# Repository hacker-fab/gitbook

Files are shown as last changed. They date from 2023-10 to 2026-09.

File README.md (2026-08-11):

---
description: the first open-source semiconductor fab.
layout:
  width: default
  title:
    visible: false
  description:
    visible: false
  tableOfContents:
    visible: true
  outline:
    visible: true
  pagination:
    visible: false
  metadata:
    visible: true
  tags:
    visible: true
  actions:
    visible: true
---

# Hacker Fab Documentation

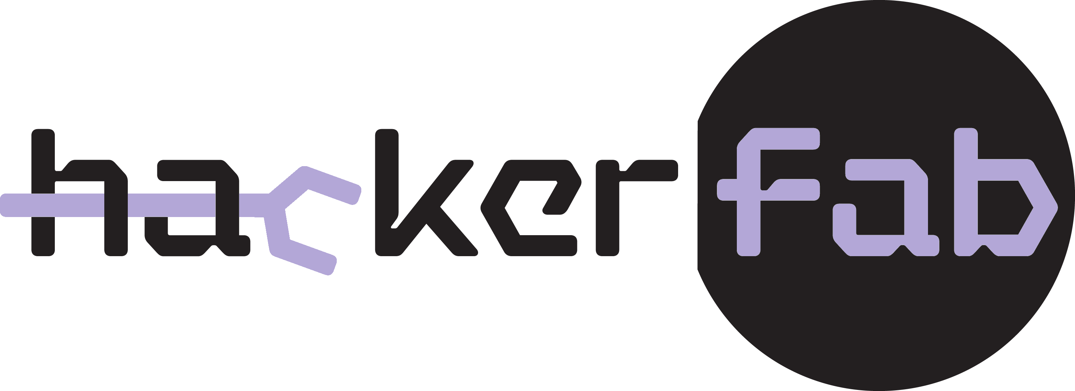
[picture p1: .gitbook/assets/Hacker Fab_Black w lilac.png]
<figure><figcaption></figcaption></figure>

<table data-view="cards"><thead><tr><th align="center"></th><th data-hidden data-card-target data-type="content-ref"></th><th data-hidden data-card-cover data-type="files"></th></tr></thead><tbody><tr><td align="center">discord.</td><td><a href="https://discord.gg/HFb3FKAxuX">https://discord.gg/HFb3FKAxuX</a></td><td></td></tr><tr><td align="center">github.</td><td><a href="https://github.com/hacker-fab">https://github.com/hacker-fab</a></td><td></td></tr><tr><td align="center">x.</td><td><a href="https://x.com/TheHackerFab">https://x.com/TheHackerFab</a></td><td></td></tr></tbody></table>

## <mark style="color:purple;">intro.</mark>

Our Goals:

1. Make a DIY version of every nanofabrication tool
2. Get there with collaborative open source hardware

Nanofabrication labs are expensive and inaccessible. Even STEM students at "prestigious institutions" have limited - if any - access to nanofabrication tools. Chips run our world. Everyone deserves access to the tools that make them. To ensure this level of access; cheap, open source, and easily replicable nanofabrication tools are needed. Labs that make and utilize these open source tools need to appear world wide. Hacker Fab is the open source fab project making this happen. As of August 2026, [**ten** Hacker Fabs have been established](https://app.gitbook.com/s/XgXjz6D0Vz2o0EOp8JO5/individual-fab-information), while others are underway. Multiple critical open source fab tools have been built, documented, and duplicated. Countless devices have been demonstrated with these tools, with documented process development.

Hacker Fab is made possible by a delocalized community of contributors. Hacker Fab can only grow to its full potential by gaining more contributors. Anyone can contribute, see the next section to learn how.

***

## <mark style="color:purple;">contributing to the hacker fab.</mark>

We communicate over [**Discord**](https://discord.gg/HFb3FKAxuX).

You don't need to build an entire fab to contribute, [**although you can**](guides/build-a-fab-to-do.md).

Read the [contribution guidelines](guides/required-reading-todo.md).

You don't need prior nanofabrication experience to create meaningful contributions.

#### How to add your work to the gitbook:

1. Hit the button that says "contribute"
2. Find the appropriate spot in the gitbook to add your work. For new projects this may be a new page, for modifications to existing work this could be an edit or amendment to existing pages. Fill in your contributed content.
   1. Note, if you download your working document(s) (google docs for example) as zipped .html files, you can them import them directly to a new gitbook page. This will maintain most of the content and formatting from your working document(s).
3. Submit a merge request; select Jay Kunselman and Alexander Hakim as reviewers.
4. Expect a message approving your merge request, or asking for revisions to your merge request.

***

## this website.

This page is a home for all shared documentation. There are enough resources here to turn an empty room into one that fabricates simple IC's in a matter of months.&#x20;

Many pages are works-in-progress. It is natural for individual contributors' work-in-progress notes to exist on google drive, notion, etc. Links to these exist at the top of each page, however these notes **move to Gitbook as soon as possible**.

Any contributor can submit change requests with a free Gitbook account. All of this is on Github, but formatted nicely here on Gitbook. You can contribute directly through Github as well.

For the most up-to-date status on everything, join the [**Discord**](https://discord.gg/HFb3FKAxuX).

***

## fab toolkit.

<table data-view="cards"><thead><tr><th></th><th></th><th></th><th></th><th></th><th></th><th data-hidden data-card-cover data-type="files"></th><th data-hidden data-card-target data-type="content-ref"></th></tr></thead><tbody><tr><td>Lithography Stepper V2</td><td><a href="fab-toolkit/patterning/lithography-stepper-v2-build-work-in-progress.md">Build </a>for $3,015</td><td><a href="standard-operating-procedures/patterning-sop-stepper-v2/">SOP</a></td><td>Carnegie Mellon</td><td></td><td></td><td><a href=".gitbook/assets/IMG_6328 (1).jpg">IMG_6328 (1).jpg</a></td><td><a href="fab-toolkit/patterning/lithography-stepper-v2-build-work-in-progress.md">lithography-stepper-v2-build-work-in-progress.md</a></td></tr><tr><td>Vacuum Spin Coater V1</td><td><a href="fab-toolkit/deposition/spin-coater-v1-build-to-do.md">Build</a> for $200</td><td><a href="standard-operating-procedures/patterning-sop-stepper-v2/vacuum-spin-coater-sop.md">SOP</a></td><td>Carnegie Mellon</td><td></td><td></td><td><a href=".gitbook/assets/spinner.jpg">spinner.jpg</a></td><td><a href="fab-toolkit/deposition/spin-coater-v1-build-to-do.md">spin-coater-v1-build-to-do.md</a></td></tr><tr><td>RF Sputtering Chamber</td><td>Build Chamber + Magnetron for $1,000</td><td>Build Power supply for $1,000 </td><td>Buy dual gas supply components for $5,000</td><td>Buy pumping system + gauge for $11,400</td><td>Carnegie Mellon</td><td><a href=".gitbook/assets/IMG_7063.jpg">IMG_7063.jpg</a></td><td></td></tr><tr><td>Thermal Evaporator V1 (work in progress)</td><td><a href="fab-toolkit/deposition/thermal-evaporator-v1-build-to-do.md">Build</a> for $15,000</td><td><a href="standard-operating-procedures/evaporator-sop.md">SOP</a></td><td>Carnegie Mellon</td><td></td><td></td><td><a href=".gitbook/assets/assembled.PNG">assembled.PNG</a></td><td><a href="fab-toolkit/deposition/thermal-evaporator-v1-build-to-do.md">thermal-evaporator-v1-build-to-do.md</a></td></tr><tr><td>Tube Furnace V1 (work in progress)</td><td><a href="https://youtu.be/oqOlrGPgng8?si=W4bGpYOg1724bw0Y">Build</a> for $200</td><td><a href="standard-operating-procedures/tube-furnace-sop.md">SOP</a></td><td>Projects in Flight</td><td></td><td></td><td><a href=".gitbook/assets/furnace.jpg">furnace.jpg</a></td><td><a href="https://www.youtube.com/watch?v=oqOlrGPgng8">https://www.youtube.com/watch?v=oqOlrGPgng8</a></td></tr><tr><td>Plasma Etcher</td><td><a href="/broken/pages/yvoQ2rocFkLU37tvrgpo">Buy</a> for $17,400</td><td><a href="standard-operating-procedures/plasma-etcher-sop.md">SOP</a></td><td>Plasma Etch PE-25</td><td></td><td></td><td><a href=".gitbook/assets/pe25-large.png">pe25-large.png</a></td><td><a href="/broken/pages/yvoQ2rocFkLU37tvrgpo">Broken link</a></td></tr><tr><td>Hot Plate</td><td><a href="https://www.amazon.com/SainSmart-Soldering-Preheating-Preheater-Intelligent/dp/B08R6XFPKR/ref=sr_1_5?crid=GQGSA76ZKKCZ&#x26;keywords=mini%2Bhot%2Bplate%2Bsoldering&#x26;qid=1701728962&#x26;sprefix=mini%2Bhot%2Bplate%2Bsoldeirn%2Caps%2C71&#x26;sr=8-5&#x26;th=1">Buy</a> for $125</td><td></td><td></td><td></td><td></td><td><a href=".gitbook/assets/2023-12-04 17_30_26-mini hot plate in hand.jpg ‎- Photos (1).png">2023-12-04 17_30_26-mini hot plate in hand.jpg ‎- Photos (1).png</a></td><td></td></tr><tr><td>3-Axis Piezo Nanopositioner</td><td><a href="/broken/pages/gS2GTDFXlq9ndyX3LUl5">Build </a>for $500</td><td></td><td></td><td></td><td></td><td></td><td></td></tr><tr><td>Electroless Plating</td><td><a href="fab-toolkit/deposition/electroless-nickel-plating.md">Build </a>for $500</td><td></td><td></td><td></td><td></td><td></td><td></td></tr></tbody></table>

<table data-view="cards"><thead><tr><th></th></tr></thead><tbody><tr><td></td></tr></tbody></table>

### verification / metrology tools.

<table data-view="cards"><thead><tr><th></th><th></th><th></th><th data-hidden data-card-cover data-type="files"></th><th data-hidden data-card-target data-type="content-ref"></th></tr></thead><tbody><tr><td>Probe Station V1</td><td><a href="/broken/pages/sr6DcGPRSb3k0lFNFZQW">Buy </a>for $15,800</td><td><a href="standard-operating-procedures/probe-station-sop.md">SOP</a></td><td><a href=".gitbook/assets/proberMPI-TS50.jpg">proberMPI-TS50.jpg</a></td><td><a href="/broken/pages/sr6DcGPRSb3k0lFNFZQW">Broken link</a></td></tr><tr><td>DIY SMU</td><td>Buy for $800</td><td><a href="fab-toolkit/metrology-characterization/semiconductor-parameter-analyzer/smu-analog-discoveries.md">SOP</a></td><td><a href=".gitbook/assets/AD3.png">AD3.png</a></td><td></td></tr><tr><td>Optical Spectrometer</td><td></td><td></td><td></td><td></td></tr></tbody></table>

### chemicals.

<table data-view="cards"><thead><tr><th></th><th></th><th></th></tr></thead><tbody><tr><td>Photoresists + Developers</td><td></td><td></td></tr><tr><td>Dielectrics</td><td></td><td></td></tr><tr><td>Conductors</td><td></td><td></td></tr><tr><td>Etchants</td><td></td><td></td></tr><tr><td>Dopant Sources</td><td></td><td></td></tr></tbody></table>

***

## background and licensing.

The Hacker Fab was inspired by [Sam Zeloof](https://www.youtube.com/@SamZeloof).

The Hacker Fab was started by Elio Bourcart, Alexander Hakim, and Sam Zeloof at Carnegie Mellon University (Thank you to CMU ECE dept, who's support catalyzed the project).

The first [Hacker Fab @ CMU](https://hackerfab.ece.cmu.edu/) is and currently managed by Matthew Moneck, Tathagata Srimani, and Jay Kunselman.

By default, all contributions use the following license stack, but may carry an additional NOTICE file depending on the origin of the contribution.

<details>

<summary>Hardware: CERN-OHL-W</summary>

For example, if you release HDL files under CERN-OHL-W and then somebody uses those files in their FPGA, when they distribute the bitstream (either putting it online or shipping a product with it) they do not to make the rest of the HDL design available under CERN-OHL-W as well.&#x20;

[https://ohwr.org/project/cernohl/wikis/faq#q-what-are-all-these-suffixes  ](https://ohwr.org/project/cernohl/wikis/faq#q-what-are-all-these-suffixes)

[https://ohwr.org/cern\_ohl\_w\_v2.pdf](https://ohwr.org/cern_ohl_w_v2.pdf)

</details>

<details>

<summary>Software: MPL v2.0</summary>

The MPL’s “file-level” copyleft is designed to encourage contributors to share modifications they make to your code, while still allowing them to combine your code with code under other licenses (open or proprietary) with minimal restrictions.&#x20;

[https://www.mozilla.org/en-US/MPL/2.0/ ](https://www.mozilla.org/en-US/MPL/2.0/)

[https://www.mozilla.org/en-US/MPL/2.0/FAQ/](https://www.mozilla.org/en-US/MPL/2.0/FAQ/)

</details>

<details>

<summary>Documentation: CC BY-SA 4.0</summary>

This license enables reusers to distribute, remix, adapt, and build upon the material in any medium or format, **so long as attribution is given to the creator**. The license allows for commercial use. If you remix, adapt, or build upon the material, you must license the modified material under identical terms. [https://creativecommons.org/licenses/by-sa/4.0/ ](https://creativecommons.org/licenses/by-sa/4.0/)[https://creativecommons.org/share-your-work/cclicenses/](https://creativecommons.org/share-your-work/cclicenses/)

</details>

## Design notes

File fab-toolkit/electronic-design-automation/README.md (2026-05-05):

---
icon: layer-group
---

# Electronic Design Automation

<table data-view="cards"><thead><tr><th></th><th data-type="content-ref"></th></tr></thead><tbody><tr><td>Mask Generation and DRC</td><td><a href="mask-generation-and-drc.md">mask-generation-and-drc.md</a></td></tr><tr><td>Device Modeling</td><td><a href="device-modeling.md">device-modeling.md</a></td></tr><tr><td>MagicVLSI</td><td><a href="magicvlsi-drc-and-lvs-wip.md">magicvlsi-drc-and-lvs-wip.md</a></td></tr></tbody></table>

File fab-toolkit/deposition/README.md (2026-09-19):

# 🧱 Deposition

<table data-view="cards"><thead><tr><th></th><th data-type="content-ref"></th></tr></thead><tbody><tr><td>Sputtering</td><td><a href="diy-rf-sputtering-chamber-cmu/">diy-rf-sputtering-chamber-cmu</a></td></tr><tr><td>ALD</td><td><a href="diy-ald/">diy-ald</a></td></tr></tbody></table>

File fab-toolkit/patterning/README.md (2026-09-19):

---
layout:
  width: default
  title:
    visible: true
  description:
    visible: true
  tableOfContents:
    visible: true
  outline:
    visible: true
  pagination:
    visible: false
  metadata:
    visible: true
  tags:
    visible: true
  actions:
    visible: true
  anchors:
    visible: true
---

# 🎥 Patterning

**For a description of what the team at CMU is working on in Spring 2025, check out** [**this document**](https://docs.google.com/document/d/1cksUbf5onK4FIIpE_ZZxUgtdfJ7OKFyU2kt76BniGkw/edit?usp=sharing)**!**

Goals of this page:

* Not to try and cover theory or industry standard, but to break the problem into first principles just enough to give context to the quantifiable parameters
* Also an opportunity to frame the problem wide enough to set the tone of thinking of these machines from the ground up (aligned with goal, don't think of industry as immutable)
* Exhaustive list of industry methods and examples
* Quantifiable end user parameters with descriptions + standardized tests

***

## Background

#### Overview

A photolithography stepper is a machine that exposes a pattern of light onto a layer of photoresist chemical on the wafer, then ‘steps’ over to the next pattern. Before each exposure, it must align with previous patterns on the wafer so that each layer of the device is in the correct position relative to the previous. The accuracy with which it can do this is called “alignment accuracy”. Alignment accuracy and optical resolution are the two most important metrics of a stepper’s performance.

There are 2 main components of our stepper: the light source and optics, and then the mechanical micropositioning stage that moves the chip itself. Alignment accuracy is a function of both the mechanical micropositioning stage and the reliability of the projector’s optomechanical components.

#### Masked vs. Maskless Lithography Systems

Commercial lithography machines use photomasks to create the image, typically made of chrome on glass. Instead, our Maskless Photolithography Stepper uses a DLP projector to create a pattern. This allows us to change patterns instantly, opening the option up for advanced techniques like tiling (making a circuit larger than one exposure field).

## Quantifiable Parameters

#### Functional Specifications: The End Product&#x20;

<details>

<summary>Developed Resolution</summary>

describe out standardized test: darkfield/brightfield, developed with AZ400K for 80s, measured pitch distance, used airforce test pattern

**Value**:&#x20;

**Tools Required for Verification**:&#x20;

**Method of Verification**:&#x20;

**Possible Variation**: Error during development (see [Patterning SOP](../../standard-operating-procedures/patterning-sop-stepper-v2/patterning-sop-stepper-v1.md))

**References**: _pics/videos_

</details>

<details>

<summary>Automation Capabilities / Throughput</summary>

what human actions are required: manual loading/unloading, choose the pattern, align manually or automatically with software

approximate area exposed per second

how much time to do one exposure, how much of that is active work vs. waiting around

</details>

&#x20;**Patterning Machine Specifications:**&#x20;

<details>

<summary>Optical Resolution</summary>

**Tools Required for Verification**: Microscope + Calibrated Camera to convert pixels to μm

**Method of Verification**: _make another page for optical resolution test?_

**Possible Variation**: misalignment of optics during assembly

**References**: _pics/_[_videos_](#user-content-fn-1)[^1]

</details>

<details>

<summary>Developed Resolution</summary>

**Tools Required for Verification**:&#x20;

**Method of Verification**:&#x20;

**Possible Variation**: Error during development (see [Patterning SOP](../../standard-operating-procedures/patterning-sop-stepper-v2/patterning-sop-stepper-v1.md))

**References**: _pics/videos_

</details>

<details>

<summary>Single Exposure Area</summary>

</details>

<details>

<summary>Approximate Exposure Time (for AZ P4210 photoresist)</summary>

**Tools Required for Verification**: AZ400K Developer Solution + Microscope

**Method of Verification**:&#x20;

**Possible Variation**: Can vary UV LED power and beam splitter ratio to decrease/increase exposure time

**References**: _pics/videos_

</details>

<details>

<summary>Mechanical Resolution - Step Size</summary>

</details>

<details>

<summary>Mechanical Resolution - Repeatability</summary>

</details>

<details>

<summary>Maximum Wafer Size</summary>

</details>

[^1]:

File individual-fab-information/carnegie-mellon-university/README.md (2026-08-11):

# Carnegie Mellon University

The [Hacker Fab @ CMU](https://hackerfab.ece.cmu.edu/) is the birthplace of the Hacker Fab initiative, and operates as an integrated course + lab. The course covers nanofabrication and device fundamentals. Students spend the majority of their time working on a project that adds a new tool/process to the fab or improves an existing one. Additionally, students participate in labs where they use the DIY tools to fab and characterize devices.

Contact(s):

* Joel Gonzalez (bgonzale@andrew.cmu.edu)
* Icey Chen (yanbing@andrew.cmu.edu)
* Rahim Malik (rahimm@andrew.cmu.edu)
* Jay Kunselman (jskunsel@andrew.cmu.edu)
* Kent Wirant (jwirant@andrew.cmu.edu)

Tooling in use:

* DIY Litho Stepper
* DIY RF Sputtering
* DIY Evaporator
* DIY Spin coater
* 2 fume hoods (lab infrastructure)
* Purchased Plasma Etcher
* Purchased Tube Furnace

Verified device capabilities:

* NMOS, 5um gate length (based on P type wafers with SiO2 and PolySi pre-fabbed by WaferPro)
* MOSCaps
* Resistors
* Diodes
* Inverters
* NAND gates

Tooling in progress:

* ALD
* 2D crystal stacking robot
* Automated Sputtering
* Automated Litho Stepper
* EDA tools

Device capabilities in progress:

* PMOS, CMOS (with in-house sputtered gate stack)

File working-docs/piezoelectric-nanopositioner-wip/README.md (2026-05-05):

# Nanopositioner - WIP

This project builds on previous work done at HackerFab, as well as concepts described in the [following paper](https://www.sciencedirect.com/science/article/pii/S2468067222000621).

Based on those designs, we decided to go with a similar mechanical approach, focusing on simplicity, compactness, and the ability to iterate quickly.

### **What it is**

This is a compact nanopositioner designed for precise motion control using a piezo actuator. The system is intended for applications like STM, optics alignment, and general nanometer-scale positioning tasks.

The mechanical design is based on linear guides using ceramic ball bearings (G5 Si₃N₄), which provide smoother and more stable motion over time compared to stainless steel balls (which tend to wear and degrade motion quality).

The current design uses:

* 2.778 mm ceramic balls
* stainless steel shafts (preferably hardened), Ø1.5 mm, length 24 mm
* thin positioning plates (\~0.25 mm) to constrain ball movement

The sliding interface is based on AlN (amorphous substrate) bonded to magnets and magnetic stainless steel (grade 430). Initially, motion is not perfectly smooth, but after a short “run-in” period (self-polishing), the system becomes significantly more stable.

<figure><figcaption></figcaption></figure>

### **Vacuum-first design**

From the beginning, this project is designed with **vacuum compatibility in mind**. That directly influences material and component choices.

We intentionally select materials that are:

* low outgassing
* mechanically stable under vacuum
* compatible with UHV-like environments (or at least not terrible in rough vacuum)

This is why we use:

* ceramic balls instead of lubricated bearings
* metal structural components instead of polymers where possible
* minimal use of adhesives (and only vacuum-compatible ones like Torr Seal where needed)
* materials like AlN for sliding interfaces

This constraint makes the design harder, but avoids having to redesign everything later for vacuum operation.

### **Piezo & Mechanics**

The actuator used is a PK2FMP2 piezo, mounted using end hemispheres and end cups. This mounting approach helps maintain alignment and reduces unwanted mechanical stress.

One critical aspect of this design is **maintaining strict axial alignment**, especially along the Z-axis.

Any deviation from the Z-axis introduces lateral forces, which:

* mechanically expand the structure
* couple motion into unwanted directions
* generate significant vibrations

This is one of the main limiting factors for stability and precision, and we are actively working on improving this.

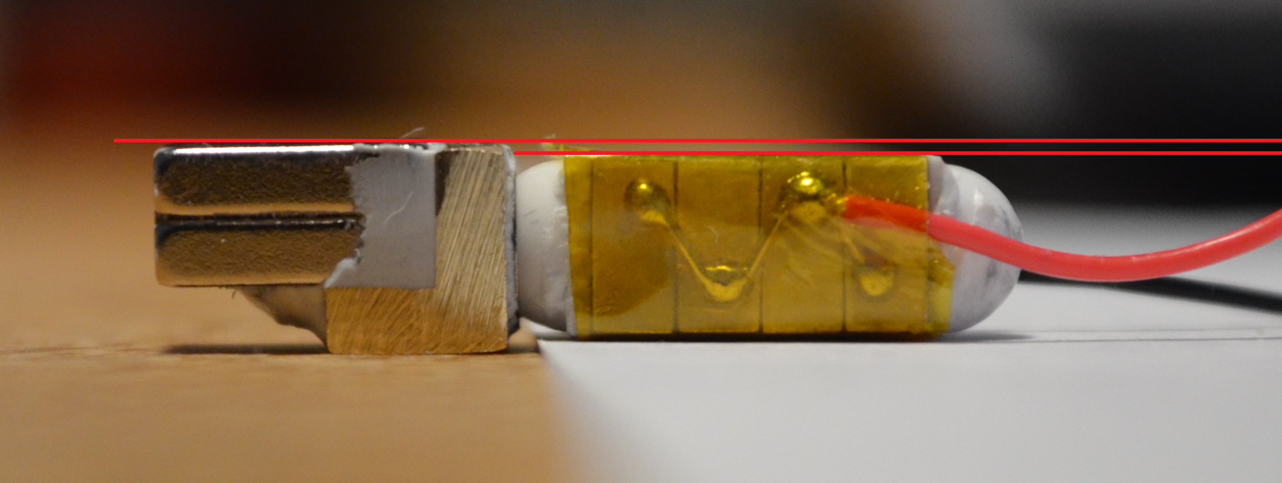
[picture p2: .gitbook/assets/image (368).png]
<figure><figcaption></figcaption></figure>

### **Electronics (WIP)**

We are currently redesigning the electronics with a focus on reducing cost and simplifying the system.

The first version of the board used **Apex PA441 amplifiers**, which cost around $25 per unit. This was originally chosen to support a wide voltage range (+100V / -50V).

However, after initial testing and switching to a different piezo, such a large range is no longer necessary. The current piezo operates up to **+60V**, which allows us to:

* simplify the driver design
* reduce cost significantly
* improve overall efficiency

We have already designed a new power supply providing **+60V / -30V**, which better matches the requirements of the current setup. At the moment, we are waiting for components to complete the new amplifier stage.

The system is designed with **opto-isolation (optocouplers)** to separate control electronics from the high-voltage section, improving robustness and reducing noise coupling.

<figure><figcaption></figcaption></figure>

### **Current Status**

This is an early prototype, but the mechanical concept is already working and gives promising results in terms of stability and resolution.

We are currently working on:

* improving electronics (cost + design)
* refining mechanical alignment (especially Z-axis stability)
* integrating an encoder (MT6835) for feedback and control

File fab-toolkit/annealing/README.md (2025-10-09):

# 🛠️ Annealing

<table data-view="cards"><thead><tr><th></th><th data-type="content-ref"></th></tr></thead><tbody><tr><td>Tube Furnace</td><td><a href="tube-furnace/">tube-furnace</a></td></tr></tbody></table>

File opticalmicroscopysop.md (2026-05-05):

# OpticalMicroscopySOP

**Document ID:** HF-QC-MIC-004\
**Prepared by:** Shreeja Gupta\
**Version:** 1.0\
**Date:** March 2, 2026

## 1. Purpose

To inspect patterned wafers using optical microscopy to verify feature quality, alignment, and dimensions after lithography and development.

Supports HackerFab fabrication workflows targeting <10 µm feature sizes using calibrated microscope measurements.

## 2. Scope

Applies to:

* Wafers after development (HF-PROC-DEV-003)
* Lithography calibration wafers
* Feature size verification and process troubleshooting

## 3. Responsibilities

* Operator: Inspect wafer and record measurements.
* Process Lead: Maintain calibration accuracy.
* Team Lead: Review results for process improvements.

## 4. Equipment & Materials

### Equipment

* Optical microscope (AmScope)
* Amscope measurement software
* Microscope stage
* Cleanroom wipes
* Computer for image capture

### Materials

* Patterned wafer
* Calibration slide (µm scale)

## 5. Safety Precautions

* Handle wafers with tweezers only.
* Avoid touching lens surfaces.
* Do not drop wafers on stage.
* Turn off illumination after use.

## 6. Calibration Requirements

Before measuring feature sizes:

1. Use a calibration slide with known µm markings.
2. Calibrate at each magnification level used.
3. Save calibration settings in software.

## 7. Procedure

{% stepper %}
{% step %}
#### 7.1 Setup

1. Turn on microscope illumination.
2. Select 5x magnification
3. Place wafer on stage.
{% endstep %}

{% step %}
#### 7.2 Focus and Locate Pattern

1. Focus using the coarse knob.
2. Adjust fine focus until the pattern is sharp.
{% endstep %}

{% step %}
#### 7.3 Inspect Pattern Quality

Check for:

* Clean edges
* No overdevelopment
* Uniform exposure
{% endstep %}

{% step %}
#### 7.4 Measure Feature Size

1. Use a calibrated measurement slide.
2. Measure multiple features.
3. Record average feature size.

Example:

* Measured smallest feature = 8.7 µm
{% endstep %}

{% step %}
#### 7.5 Capture Images

1. Save screenshots at100% zoom (important for accurate scaling).
2. Include a scale bar.
3. Name the file with the date.

Example:2026-03-02\_HFLogo\_8sExposure\_4000rpm.png
{% endstep %}
{% endstepper %}

## 8. Expected Results

* Sharp, well-defined patterns.
* Feature sizes within the expected range.
* Verification of lithography calibration.

## 9. Troubleshooting

| Problem               | Cause             | Fix                    |
| --------------------- | ----------------- | ---------------------- |
| Blurry image          | Out of focus      | Refocus stage          |
| Wrong feature size    | Calibration error | Recalibrate microscope |
| Uneven patterns       | Spin coat issue   | Check SC SOP           |
| Overdeveloped pattern | Too long dev time | Adjust DEV SOP         |

## 10. Notes

* Always recalibrate after changing magnification.
* Keep image records for process tracking.
* Use microscopy results to tune exposure dose and spin speed.

## 11. Revision History

| Version | Date          | Changes       |
| ------- | ------------- | ------------- |
| 1.0     | March 2, 2026 | Initial draft |

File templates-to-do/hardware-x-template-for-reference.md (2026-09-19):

---
hidden: true
---

# Hardware X Template (for reference)

<br>

1\.  Hardware in context

Write a short description of the hardware and provide context, i.e., describe similar open hardware and proprietary equipment in the field.

<br>

2\.  Hardware description

Describe your hardware, highlighting the customization rather than the steps involved in the procedure. Explain how  it  differs  from  other  hardware  and  the  advantages  it  offers  over  pre-existing  methods.  For  example,  how does this hardware compare to other hardware in terms of cost or ease of use, or how can it be used to develop further designs in a particular area?&#x20;

Add 3-5 bullet points which broadly explain to other researchers - inside or outside of the original user community - how the hardware could help them, with either standard or novel laboratory tasks.

<br>

Design files

Your design files should be editable - see OSHWA’s open source definition of ‘Documentation’ for further details. You must then either:

* Upload your design files to one of the three approved online repositories - Mendeley Data (instructions), the  Open  Science  Framework  (instructions)  or  Zenodo  (instructions).  We  recommend  this  option  as  the repositories support versioning of files.
* Upload your design files as supplementary materials (e.g., CAD files, videos. . . )  to Hardware X’s online editorial system when you submit your manuscript.
* Include your design files in the body of the manuscript (e.g., as figures).

<br>

CAD files:

You are encouraged to use free and open source software packages for creating the  files.  For  CAD files, OpenSCAD, FreeCAD, or Blender  are  encouraged, but, if these are  not  available, we accept source files from proprietary CAD packages, such as Autocad or Solidworks, and other drawing packages.

<br>

3D printing:

Supplementary files that facilitate digital replication of the devices are encouraged; for example, STL files for 3D printing components. We recommend uploading CAD files to the NIH 3D Print Exchange as Custom Labware and then entering the link here.

<br>

Electronics:

PCB layouts and other electronics design files can be uploaded to the Open Hardware  Repository or other repositories or as supplementary materials.

<br>

Software and firmware:

All software files used in the design and operation of the hardware should be included in the repository. Provide a description of the software and firmware and use extensive comments in the code.&#x20;

<br>

3\.  Design files summary

Complete a separate row for each design file associated with your hardware (including the primary design files). Any empty rows should be deleted.

<br>

<br>

| Design filename             | <p>File type</p><p><br></p>     | <p>Open source license</p><p><br><br></p>                                                                               | <p>Location of the file</p><p><br></p>                                                           |
| --------------------------- | ------------------------------- | ----------------------------------------------------------------------------------------------------------------------- | ------------------------------------------------------------------------------------------------ |
| For  example: Design file 1 | E.g. CAD  file, figures, videos | All designs must be submitted under an open hardware license.  Enter the corresponding open source license for the file | Either enter    the    URL for the  repository  or  the  sentence: ”Available with the article”. |

<br>

<br>

For each design file listed in the summary table above, include a short description of the file below (just one or two sentences per design file).

<br>

Bill of materials

If  your  bill  of  materials  is  long  or  complex,  you  can  upload  the  details  in  an  editable  spreadsheet, e.g., ODS file type, Excel spreadsheet or PDF file, to an open access online location, such as the Open Science Framework repository.  Include the link here.  Alternatively, the bill of materials can be submitted alongside your manuscript as supplementary material.

<br>

<br>

4\.  Bill of materials summary

Complete  a  separate  row  for  each  component  of  your  hardware  –  all  components  associated  with  a  cost  should be listed and any empty rows should be deleted.

<br>

<br>

| Designator                                                                                                                                                                                      | Component           | Number          | Cost per unit - currency            | <p>Total cost -currency</p><p><br></p> | Source of Materials                 | Material Type                                                                                                                                                                                                                             |
| ----------------------------------------------------------------------------------------------------------------------------------------------------------------------------------------------- | ------------------- | --------------- | ----------------------------------- | -------------------------------------- | ----------------------------------- | ----------------------------------------------------------------------------------------------------------------------------------------------------------------------------------------------------------------------------------------- |
| <p>If possible,</p><p>use the same designator  here as you use in the associated</p><p>design file.If that’s not possible, you will need to explain the  relationship</p><p>between the two</p> | Name of component 1 | Number of units | Cost per unit and the currency used | Total cost and the currency used       | If possible, direct purchasing link | <p>Select from:</p><p>-Metal</p><p>-Semi-</p><p>conductor</p><p>-Ceramic</p><p>-Polymer</p><p>-Biomaterial</p><p>-Organic</p><p>-Inorganic</p><p>-Composite</p><p>-Nanomaterial</p><p>-Semiconductor</p><p>-Non-specific</p><p>-Other</p> |

<br>

You can use this space for any additional descriptions of the materials used.

<br>

<br>

5\.  Build instructions

Provide detailed, step-by-step construction instructions for the submitted hardware:

* Include all necessary information for reproducing it.
* Explain and (when possible) characterize design decisions.  Include any design alternatives you created.
* Use visual instructions such as schematics, images and videos.
* Clearly reference design files and component parts described in the Design file summary and the Bill of materials summary
* Highlight any potential safety concerns.

<br>

6\.  Operation instructions

Provide detailed, step-by-step instructions for the safe and proper operation of the hardware.

* Use visual instructions, as necessary.
* Highlight any potential safety hazards.

<br>

7\.  Validation and characterization

Demonstrate the operation of the hardware and characterize its performance for a specific scientific application.

* Highlight a relevant use case.
* If possible, characterize performance of the hardware over operational parameters.
* Create a bulleted list describing the capabilities (and limitations) of the hardware.  For example, load and operation time, spin speed, coefficient of variation, accuracy, precision, etc

\
<br>

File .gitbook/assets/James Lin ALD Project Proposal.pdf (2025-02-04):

18-469D/18-669D - Hacker Fab | Spring 2025

# Proposal & Plan:

## ALD Precursor Delivery System

James Lin

## Background

The Precursor Delivery System is responsible for delivering the precursors of I2O3 and SnO2 (TMIn and TDMASn respectively), H2O, and the N2 carrier gas to the ALD chamber.

The delivery system is designed to pulse the precursor chemicals at specific pressures and time intervals to deliver the right chemical at each state of the deposition process. It is also designed to facilitate the flow of the carrier gas at a specific temperature and flow rate for both chemical delivery and purging on the wafer surface.

This is all done in order to facilitate the growth of high quality ITO thin films in the ALD chamber.

The delivery system must be rated and sealed for the overall vacuum requirement of the entire ALD system of 100 mTorr. In addition, due to the precursor chemicals being pyrophoric, materials that interact with the chemicals must also be considered in order to comply with lab safety requirements.

The overall ALD Delivery System will consist of two main parts:
- Delivery System
- Delivery Storage

1

## Delivery System

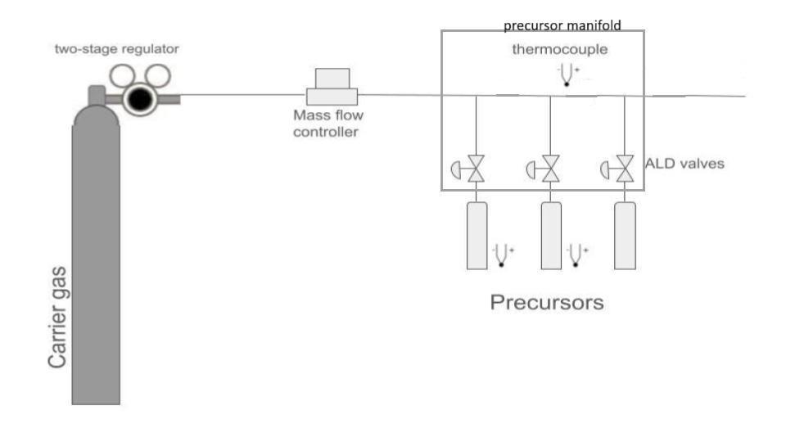
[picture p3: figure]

Technical requirements
- Material Selection:
- Compatible with pyrophoric chemicals and corrosion resistant
- Thermal:
- TMIn and TDMASn bubblers heated to 60C
- Needs possibility for 20C for TMIn and 45C for TDMASn
- Delivery line capable of maintaining fluid temperature of 60C up to ALD chamber
- Fluid Delivery and Vacuum:
- Delivery line rated for 100 mTorr vacuum
- Carrier gas delivered at 10 - 40 sccm
- Compatible with either N2 or Ar
- ALD valves able to pulse for 3-0.625 s
- Measurement:
- Thermocouple capable of accurate fluid temperature measurement
- Integration with DAQ and electronics
- Integration with the ALD chamber
- Minimize cost where possible

2

What has been completed/purchased
- Dual stage regulator (NOT ORDERED)
- Steps down from cylinder pressure (~2000 psi) to operating pressure for Mass Flow Controller (<70 psi)
- 100 SCCM flow controller
- Chemical ampules
- From CMU Nanofab
- Swagelok ALD3 valves and manifold
- From CMU Nanofab
- inlet = ¼” female VCR
- outlet = ¼” male VCR
- Stainless steel tubing
- Male and female VCR to male fittings
- VC face seal metal gaskets
- KF25 to ¼” tube fitting
- Interface with vacuum
- Heating tape (DOESN’T WORK)

Since most of the central components have already been procured and critical materials and fittings have been decided, further development would be focused on tube routing, possible thermal insulation, thermocouple integration, and construction.

3

Major deliverables
- Full CAD of delivery system
- Fittings locations and tubing geometry accurate to real life setup
- Communication with electronics for sensor placement and wiring plan
- Check for assembly operations and integration with Delivery Storage
- Assembly of delivery system
- Troubleshoot any potential problems with integrating electronics
- Testing for performance of assembly under vacuum
- Ensure that the system complies with safety and technical requirements during use
- Testing heating element and sensors
- Ensure temperature, flow rate, and pressure targets are met
- Ensure that controls are able to read accurate data
- Documentation
- Design process, analysis
- Manufacturing and assembly instructions
- BOM

Things to consider
- Overall dimensions of proposed locations of ALD station
- Heating should be maintained for all lines downstream of precursor
- Must avoid condensation and precursor build up so line doesn’t explode
- Thermocouple placement should be on tube surface as to not disrupt fluid

flow
- Research temperature values also measure at tube
- ¼” tube should not have steady state and conduction loss problems
- Operations of assembly
- We do not want to get tubings that don’t fit
- Integration with delivery storage and electronic components
- Heating block vs heating tape
- Heating block is made to fit manifold but very heavy
- Heating tape would need some thinking to figure out how to wrap manifold

4

## Delivery Storage

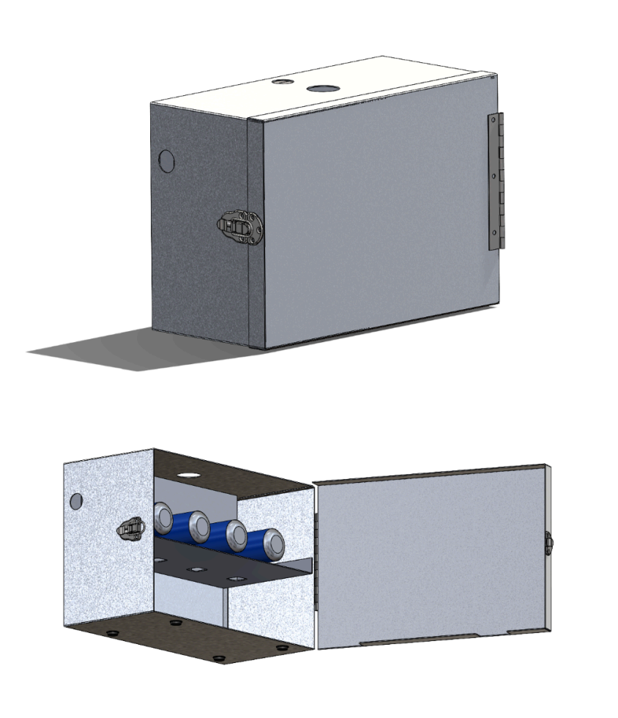
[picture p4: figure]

Technical Requirements
- Storage Capacity:
- Holds the precursor manifold with three ALD valves and three gas ampules
- Potentially has room for mass flow controller in the future
- Packaging:
- Contains holes to attach proper fittings for an exhaust connection, carrier gas inlet, and a gas outlet
- Potentially need pass throughs to account for wiring
- Leave room for either heating block or heating tape/alternative heating options
- Materials:
- Made out of aluminum for precursor compatibility
- Ergonomics:
- Ampoules should be easy to access in order for simpler replacement when necessary
- Manufacturing:
- Minimize time to manufacture and assemble
- Design needs to be easily replicable
- Allow design to be manufactured with precision
- Minimize cost

5

What has been completed/purchased
- Prototype enclosure partially made with bent sheet metal and riveted

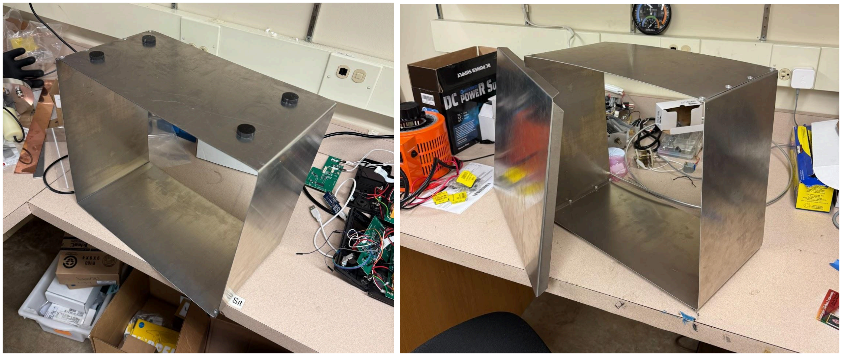
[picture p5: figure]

- Draw latches
- Adhesive bumpers
- Excess of 0.050” thick 5052 AL
- Rivet tool and blind rivets (3/16”)

Certain decisions like materials have already been made. The prototype is not yet completed, and several recommendations for improvements have been made regarding the design from F24. Therefore I will be focused on both possible redesign/modifications of components as well as aiming to finish the assembly of the Delivery Storage.

6

Major Deliverables
- Examine results from F24 and decide on necessary changes
- Decide on the scope of redesigning components
- Take into consideration the manufacturing lessons learned
- Communicate with team to include capacity for future use
- Full updated CAD of Delivery Storage
- Check for compliance with available space in the lab
- Implement any design changes to better meet technical requirements
- Designing for manufacturing
- Integration with Delivery System CAD
- Manufacturing plan
- Consider ease of manufacturing and assembly
- Review outsourcing decision based on timeline and cost
- Fully assembled storage prototype
- Aim to reduce eort and time for manufacturing
- Prior experience with machining and access to shops should help with making components
- Testing for interferences and manufacturing issues
- Working with electronics and ALD chamber for integration
- Documentation
- Design process, analysis
- Manufacturing and assembly instructions
- BOM

7

Things to consider
- Hardware choice
- Is the cost-benefit of rivets outweighed by nuts and bolts being easier to install?
- Adhesive could also be an option, but may have issues with chemical compatibility
- Structural considerations
- Noticed the prototype is a bit floppy, also the AL is relatively thin
- Thicker AL can improve rigidity, but costs more
- Structural support both internally and externally can be considered ■ External support doesn’t need to meet chemical compatibility requirements due to AL walls as barriers
- Potential for low cost materials like PLA 3D prints
- Shelf redesign
- How to best fixture ampules and make them easy to replace?
- Replication and outsourcing
- Can we find a cheaper alternative for outsourcing sheet metal manufacturing?
- Can we expect others reading our documentation to easily construct the enclosure?
- Sheet metal manufacturing
- Potential design changes that can reduce manufacturing time by reducing number of sheet metal bent parts
- Packaging
- Heater choice:
■ Can we make a decision early on between heater block and heater tape?
- MFC is probably not going in the enclosure
- Do not need to plan for more than three ampules
- Clear communication about wire routing and hole placements

8

## Timeline

Deadline | Delivery System | Delivery Storage
1/28/25 | Document and understand physical design space in the lab + Order new heating tape, regulator, and KF25 fitting | Look at heating block and get mass & CAD
2/2/25 | Finalize design decisions
2/9/25 | CAD rev 1
2/15/25 | Full BOM + ordering
2/16/25 | Presentation 1
2/18/25 | Manufacturing and Assembly Plan
2/23/25 | Tubes cutting | Sheet metal bending
2/26/25 | | Machining + other manufacturing
2/28/25 | Assembly
3/1/25 | Testing for vacuum and thermals | Testing for reliability and ergonomics
TBD | Make changes as necessary
3/23/24 | Presentation 2
4/25/24 | Documentation
4/27/24 | Final Presentation

9

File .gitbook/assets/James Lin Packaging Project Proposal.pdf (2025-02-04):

18-469D/18-669D - Hacker Fab | Spring 2025

# Proposal & Plan:

## IC Packaging

James Lin

## Background

Hacker Fab currently utilizes the probing station available at CMU for electrical characterization of its ICs, but these machines have proven dicult to both access and operate. Consequently, the team is developing a DIY probing station at a much lower price in hopes of bringing this capability in house. However, as our ICs eventually get more complex and start to increase in IO counts, characterization with a probing station will also require more time and eort.

Typical semiconductor packaging process goes through the following steps:

- Wafer-level probing for known good die (KGD)
- Wafer back grinding
- Wafer dicing
- Die pick & sort
- Die attach to package
- Wire bonding or flip chip bonding
- Package encapsulation
- Packaged die test
- Final assembly onto printed circuit board (PCB)

(Hacker Fab: Packaging, Robert M. Radway, 2024)

1

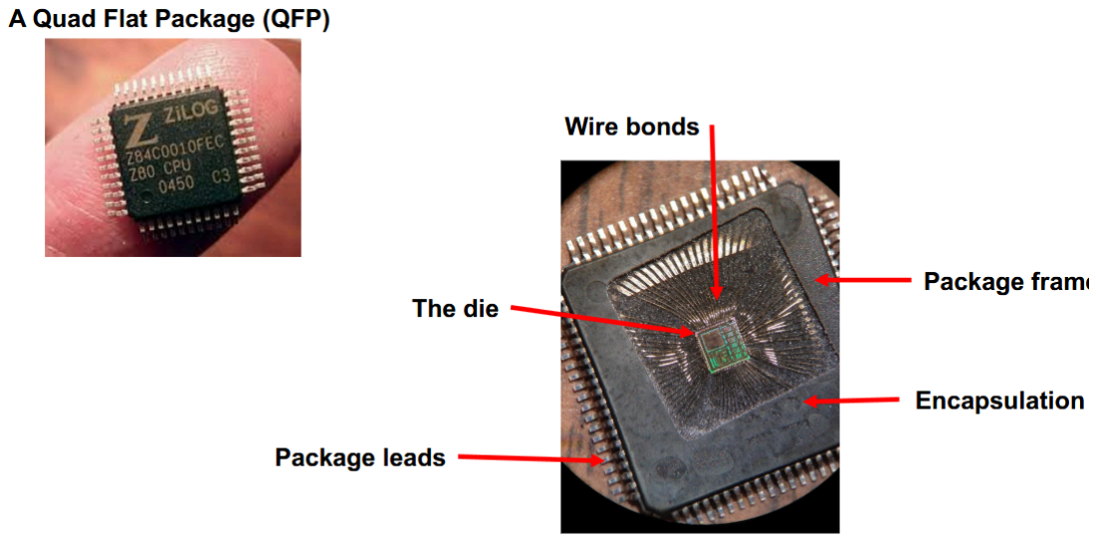
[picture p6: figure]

(also from Radway’s presentation)

Since Hacker Fab is not geared towards high throughput and focuses on ease of manufacturing and accessibility, this process flow will likely be shortened to the following:

- Wafer-level probing for known good die (KGD) - optional
- Depends on availability of probe station
- Wafer dicing
- Can be easily done in house
- Die attach to package
- Required to hold IC mechanically in package
- Wire bonding
- We will be using wire bonders in the MEMs lab at CMU
- Package encapsulation
- Required to protect IC from the environment
- Packaged die test + Final assembly onto PCB
- Ultimate goal of the project to test IC on a PCB

As part of the metrology team, I will be working on a process to package our ICs so that it can eventually interface with an Analog Discovery 3 via a PCB, thus not only allowing us to characterize ICs with large IO counts quickly, but also allowing us to better test the entire IC’s performance in the future. This capability will allow the team to further vertically expand in the IC manufacturing process.

2

## IC Packaging Process

Technical requirements
- Lead Frame and IC Pads:
- Both the lead frame and IC pads must be compatible with the wire bonding process and materials available in the MEMs lab
- Lead frame and its leads should be mechanically strong enough for normal handling and installation, as well as compatible with soldering
- IC pads needs to be compatible with Hacker Fab manufacturing and design capabilities
- Wire bonding:
- Wires used should be compatible for bonding with substrate material
- Parasitic resistance:
- All conducting materials should not introduce high parasitic resistance in order to preserve granularity of characterization data
- Encapsulation:
- Be mechanically strong enough to withstand handling and high temperatures from both IC power dissipation and soldering
- Electrically insulate the IC the environment without unplanned conduction paths
- Coecient of Thermal Expansion (CTE):
- All materials should have closely matched CTEs to the IC substrate to prevent mechanical failure from thermal stresses
- Package selection:
- Spacing and dimension of leads should closely match existing packages to successfully mount on standard PCB boards or bread boards
- Minimize cost where possible

3

The process and design of the IC package will be developed from the ground up, which would require extensive research on industry practices and literature.

Major deliverables
- CAD of encapsulation and lead frame
- Full manufacturing process flow
- Tools, materials, parameters
- Test and validate wire bonding recipes done in the MEMs lab
- Prototype with single transistor IC
- Prototype with multi-transistor ICs
- Stress testing package for thermal and moisture resistance
- Integration with process and metrology test plans

4

Things to consider
- Planned IC dimensions for current capabilities
- Confirmed 1 cm x 1 cm
- This may necessitate a costume package inspired by industry
- Lead frame manufacturing method
- Very few sources are easily available for purchase
- Possibility for in house etching, but stepper field size is not large enough for entire lead frame
- Cannot do with TechSpark laser cutter bc reflective metal
■ Online sources says fiber laser or oxygen-high powered laser are preferred but don’t know if available on campus
- PCB mill is likely since people have used it to do lead frames before ■ Waiting on Joel to check
- Encapsulation manufacturing
- May need very specialized epoxy due to CTE concerns
- Might explore possibility of 3D printing, but has resolution and thermal concerns
- Resin printing is an option
■ Joel can set up his printer in oce
■ Ideate might also let us do it
- Adhesives:
- Might also be specialized and hard to source depending on requirement
- Logistics with team:
- Need to lock down specific materials and dimensions on IC side early on to begin testing process for wire bonding and address other design requirements
- Week 4-6 EDA will be planning and finalizing test plan
■ Talk to Gongwei
- Need to figure out who is making multi-transistor IC and what circuit/IO it will have
- Wire bonding:
- Want to test with pad material and stack that matches final chip ■ Pad peel-o is current biggest concern
- Can probably start rudimentary tests soon by just making a grid on silicon with thermal evaporated Al

5

## Timeline

Deadline | Deliverable
1/28/25 | Get familiarized with wire bonder in MEMS Lab
1/31/24 | Pick package to reference for design
2/7/25 | Finalize pad dimensions with EDA team
2/8/25 | Wire bonding test with Al on Si
2/13/25 | Lead frame and encapsulation design
2/16/25 | Presentation 1
2/19/25 | Lead frame and encapsulation manufactured
2/20/25 | Work with EDA to finalize test plan
2/23/25 | 1 transistor chip manufactured
2/28/25 | 1 transistor package assembled
3/7/25 | Testing with 1 transistor package
3/9/25 | Lead frame and encapsulation design
3/14/25 | Lead frame and encapsulation manufactured
3/26/25 | Presentation 2
TBD | Multi-transistor IC manufactured
TBD | Multi-transistor IC assembled
TBD | Multi-transistor IC tested
4/25/25 | Documentation
4/27/25 | Final Presentation

6

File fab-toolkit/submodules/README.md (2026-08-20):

# 🏘️ Submodules

<table data-view="cards"><thead><tr><th></th><th data-type="content-ref"></th></tr></thead><tbody><tr><td>Piezo Nanopositioner (stick slip)</td><td><a href="../../working-docs/piezoelectric-nanopositioner-wip/piezo-nanopositioner-stick-slip.md">piezo-nanopositioner-stick-slip.md</a></td></tr></tbody></table>

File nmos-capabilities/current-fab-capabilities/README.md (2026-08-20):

---
description: Last Updated March 2026
layout:
  width: default
  title:
    visible: true
  description:
    visible: true
  tableOfContents:
    visible: true
  outline:
    visible: true
  pagination:
    visible: false
  metadata:
    visible: true
  tags:
    visible: true
  actions:
    visible: true
---

# ✨ Self Aligned NMOS

* 952 Transistors per Chip
* 94% Yield
* 1.26V Threshold Voltage
* 5 um gate length

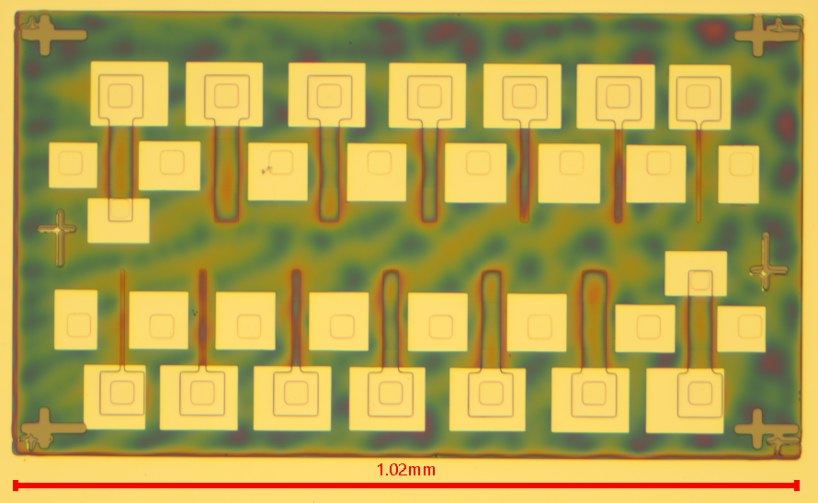
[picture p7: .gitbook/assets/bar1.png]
<figure><figcaption></figcaption></figure>

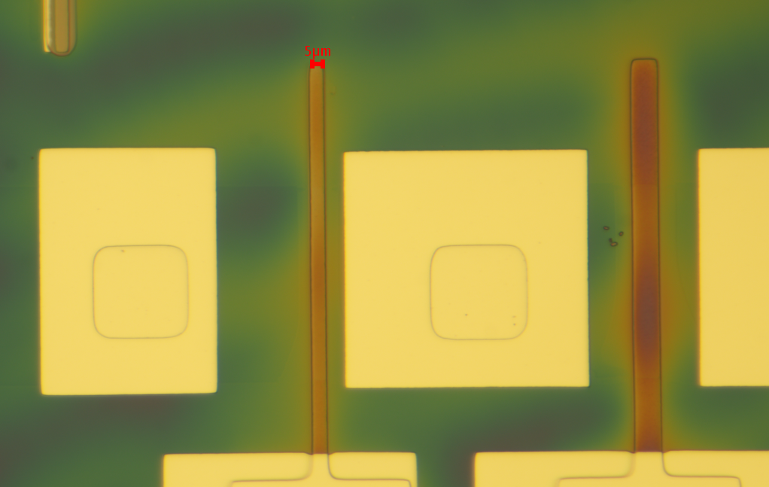
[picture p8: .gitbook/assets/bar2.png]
<figure><figcaption></figcaption></figure>

<figure><figcaption></figcaption></figure>

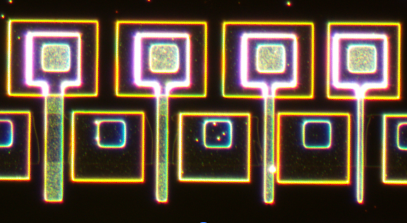
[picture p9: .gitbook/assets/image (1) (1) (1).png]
<figure><figcaption></figcaption></figure>

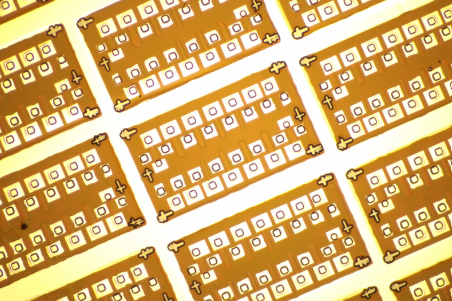
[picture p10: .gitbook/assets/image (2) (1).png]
<figure><figcaption></figcaption></figure>

Process in Fabublox:

{% embed url="https://www.fabublox.com/process-editor/f52fe668-594d-4a94-bfb1-b1e3ce845f38" %}

| Step #          | Step Name                    | Parameters                                                                                                                                       | Comments                                                                                                                                                                                                             | Layer Stacks                                                                                                                                                                                                                                                                                                                                                                                                                                                                                                                                                                                                                                                                                                                                                                                                                                                                                                                                                                                                                                                                                                                                                                                                                                                                                                                                                                                                                                                                                                                                                                                                                                                                                                                                                                                                                                                                                                                                                                                                                                                                                                                    |
| --------------- | ---------------------------- | ------------------------------------------------------------------------------------------------------------------------------------------------ | -------------------------------------------------------------------------------------------------------------------------------------------------------------------------------------------------------------------- | ------------------------------------------------------------------------------------------------------------------------------------------------------------------------------------------------------------------------------------------------------------------------------------------------------------------------------------------------------------------------------------------------------------------------------------------------------------------------------------------------------------------------------------------------------------------------------------------------------------------------------------------------------------------------------------------------------------------------------------------------------------------------------------------------------------------------------------------------------------------------------------------------------------------------------------------------------------------------------------------------------------------------------------------------------------------------------------------------------------------------------------------------------------------------------------------------------------------------------------------------------------------------------------------------------------------------------------------------------------------------------------------------------------------------------------------------------------------------------------------------------------------------------------------------------------------------------------------------------------------------------------------------------------------------------------------------------------------------------------------------------------------------------------------------------------------------------------------------------------------------------------------------------------------------------------------------------------------------------------------------------------------------------------------------------------------------------------------------------------------------------- |
|                 |                              |                                                                                                                                                  |                                                                                                                                                                                                                      |                                                                                                                                                                                                                                                                                                                                                                                                                                                                                                                                                                                                                                                                                                                                                                                                                                                                                                                                                                                                                                                                                                                                                                                                                                                                                                                                                                                                                                                                                                                                                                                                                                                                                                                                                                                                                                                                                                                                                                                                                                                                                                                                 |
| Unnamed Section |                              |                                                                                                                                                  |                                                                                                                                                                                                                      |                                                                                                                                                                                                                                                                                                                                                                                                                                                                                                                                                                                                                                                                                                                                                                                                                                                                                                                                                                                                                                                                                                                                                                                                                                                                                                                                                                                                                                                                                                                                                                                                                                                                                                                                                                                                                                                                                                                                                                                                                                                                                                                                 |
| 0               | Substrate Stack              | <p>PolySi: 500 nm<br>SiO2: 20 nm<br>Si (lightly p doped): 525 µm</p>                                                                             |                                                                                                                                                                                                                      | ![]()                                                                                                                                                                                                                                                                                                                                                                                                                                                                                                                                                                                                                                                                         |
| 1               | Acetone + IPA Clean (N2 dry) | <p>Cleaning Agent: Acetone then IPA<br>Ultra-Sonication: false</p>                                                                               | Squirt with Acetone, then IPA, then dry the surface with the N2 gun.                                                                                                                                                 | ![]()                                                                                                                                                                                                                                                                                                                                                                                                                                                                                                                                                                                                                                                                         |
| 2               | Spin-On Dopant               | <p>Spin-On Dopant Name: P504<br>Dopant Type: N<br>Spin Speed: 4000 rpm<br>Spin Time: 20 secs</p>                                                 | <p>P504 from Filmtronics<br>must use filtered syringe tips</p>                                                                                                                                                       | ![]()                                                                                                                                                                                                                                                                                                                                                                                                                                                                                                                                                                                                     |
| 3               | Dopant Diffusion             | <p>Diffusion Time: 15 mins<br>Diffusion Temperature: 1100 °C<br>Environmental: false</p>                                                         | In tube furnace with fused quartz tube                                                                                                                                                                               | ![]()                                                                                                                                                                                                                                                                                                                                                                                                                                                                                                 |
| 4               | Wet-Etch                     | <p>Etch Time: 10 mins<br>Etching Agent(s): 6:1 BOE<br>Etch Temperature: 25 °C</p>                                                                | <p>BOE is HF + Ammonium Fluoride<br><br>DI water rinse after etch</p>                                                                                                                                                | ![]()                                                                                                                                                                                                                                                                                                                                                                                                                                                                                                                                                                                 |
| 5               | Acetone + IPA Clean (N2 dry) | <p>Cleaning Agent: Acetone then IPA<br>Ultra-Sonication: false</p>                                                                               | Squirt with Acetone, then IPA, then dry the surface with the N2 gun.                                                                                                                                                 | ![]()                                                                                                                                                                                                                                                                                                                                                                                                                                                                                                                                                                                 |
| 6               | HMDS Vapor Prime             | <p>Deposited Monolayer: HMDS<br>Layer Thickness: 5 Å</p>                                                                                         | <p>Not Using an actual vapor primer.<br><br>Spin @ 3000 rpm for 20 s<br>bake at 100C for 20 s</p>                                                                                                                    | ![]()                                                                                                                                                                                                                                                                                                                                                                                                                                                                                                                                             |
| 7               | Spin Resist                  | <p>Resist: AZ P4210<br>Resist Type: Positive<br>Spin Speed: 4000 rpm<br>Spin Time: 30 secs</p>                                                   |                                                                                                                                                                                                                      | ![]()                                                                                                                                                                                                                                                                                                                                                                                                                                                                                     |
| 8               | Bake                         | <p>Bake Temperature: 100 °C<br>Bake Time: 90 secs</p>                                                                                            |                                                                                                                                                                                                                      | ![]()                                                                                                                                                                                                                                                                                                                                                                                                                                                                                     |
| 9               | Stepper Lithography          |                                                                                                                                                  | Pattern 1 -Defining Gates                                                                                                                                                                                            | ![]()                                                                                                                                                                                                                                                                                                                                                                                             |
| 10              | Develop                      | <p>Developer: AZ 400K 3:1 (DI water : developer)<br>Develop Time: 30 secs<br>Develop Temperature: 25 °C</p>                                      | Develop time may vary, use current stable patterning process. Modulate exposure time and develop time as needed to achieve good pattern resolution                                                                   | ![]()                                                                                                                                                                                                                                                                                                                                                                                                                         |
| 11              | ICP-RIE                      | <p>Etch Time: 90 secs<br>Etch Gas Composition: SF6<br>Gas Flows and Ratios: 10 sccm<br>RF Power or Voltage: 100 Watts<br>Sidewall Angle: 0 °</p> |                                                                                                                                                                                                                      | ![]()                                                                                                                                                                                                                                                                                                                                                                                                                                                                 |
| 12              | Wet Strip Resist             | Stripping Agent(s): Acetone then IPA                                                                                                             | Squirt with acetone, then IPA, then dry with N2 gun                                                                                                                                                                  | ![]()                                                                                                                                                                                                                                                                                                                                                                                                                                                                                                                                                 |
| 13              | Plasma Descum                | <p>Gas composition: O2 10 SCCM<br>RF Power: 100 Watts<br>Time: 2400 secs</p>                                                                     | Alternatively, a shorter clean can be done before resist strip.                                                                                                                                                      | ![]()                                                                                                                                                                                                                                                                                                                                                                                                                                                                                                                                                 |
| 14              | Wet-Etch                     | <p>Etch Depth: 20 nm<br>Etch Time: 20 secs<br>Etch Rate: 80 nm/s<br>Etching Agent(s): 6:1 BOE (HF)</p>                                           | <p>BOE is HF + Ammonium Fluoride<br><br>DI water rinse after etch</p>                                                                                                                                                | ![]()                                                                                                                                                                                                                                                                                                                                                                                                                                                                                                                                                                         |
| 15              | Spin-On Dopant               | <p>Spin-On Dopant Name: P504<br>Dopant Type: N+<br>Spin Speed: 4000 rpm<br>Spin Time: 20 secs</p>                                                | <p>P504 from Filmtronics<br>must use filtered syringe tips<br></p>                                                                                                                                                   | ![]()                                                                                                                                                                                                                                                                                                                                                                                                                                                                                 |
| 16              | Bake                         | <p>Bake Temperature: 200 °C<br>Bake Time: 10 mins</p>                                                                                            |                                                                                                                                                                                                                      | ![]()                                                                                                                                                                                                                                                                                                                                                                                                                                                                                 |
| 17              | HMDS Vapor Prime             | <p>Deposited Monolayer: HMDS<br>Layer Thickness: 5 Å</p>                                                                                         | <p>Not Using an actual vapor primer.<br><br>Spin @ 3000 rpm for 20 s<br>bake at 100C for 20 s</p>                                                                                                                    | ![]()                                                                                                                                                                                                                                                                                                                                                                                                                     |
| 18              | Spin Resist                  | <p>Resist: AZ P4210<br>Resist Type: Positive<br>Spin Speed: 4000 rpm<br>Spin Time: 30 secs</p>                                                   |                                                                                                                                                                                                                      | ![]()                                                                                                                                                                                                                                                                                                                                                                         |
| 19              | Bake                         | <p>Bake Temperature: 100 °C<br>Bake Time: 90 secs</p>                                                                                            |                                                                                                                                                                                                                      | ![]()                                                                                                                                                                                                                                                                                                                                                                         |
| 20              | Stepper Lithography          | Exposure time: 8 secs                                                                                                                            | Pattern 2 N well (source/drain) region defining pattern. Note, this may overlap with the gate area and further effect PolySi dopant concentration.                                                                   | ![]()                                                                                                                                                                                                                                             |
| 21              | Develop                      | <p>Developer: AZ 400K 3:1 (DI water : developer)<br>Develop Time: 60 secs<br>Develop Temperature: 25 °C</p>                                      | Develop time may vary, use current stable patterning process. Modulate exposure time and develop time as needed to achieve good pattern resolution.                                                                  | ![]()                                                                                                                                                                                                                                                                                                                 |
| 22              | Wet-Etch                     | <p>Etch Time: 10 secs<br>Etching Agent(s): BOE 6:1 (HF)</p>                                                                                      |                                                                                                                                                                                                                      | ![]()                                                                                                                                                                                                                                                                                                             |
| 23              | Wet Strip Resist             | Stripping Agent(s): Acetone then IPA                                                                                                             | Squirt with acetone, then IPA, then dry with N2 gun                                                                                                                                                                  | ![]()                                                                                                                                                                                                                                                                                                                                                                                                                 |
| 24              | Dopant Diffusion             | <p>Diffusion Time: 30 mins<br>Diffusion Temperature: 1100 °C<br>Environmental: false</p>                                                         |                                                                                                                                                                                                                      |                                                                                                                                                                                                                                                                                                                                                                                                                                                                                                                                                                                                                                                                                                                                                                                                                                                                                                                                                                                                                                                                                                                                                                                                                                                                                                                                                                                                                                                                                                                                                                                                                                                                                                                                                                                                                                                                                                                                                                                                                                                                                |
| 25              | Wet-Etch                     | <p>Etch Time: 10 mins<br>Etching Agent(s): 6:1 BOE (HF)</p>                                                                                      |                                                                                                                                                                                                                      | ![]()                                                                                                             |
| 26              | Spin-Coat                    | <p>Material: 700B<br>Spin Speed: 4000 rpm<br>Spin Time: 20 secs</p>                                                                              | 700B from filmtronics                                                                                                                                                                                                | ![]()                                     |
| 27              | Bake                         | <p>Bake Temperature: 200 °C<br>Bake Time: 10 mins</p>                                                                                            |                                                                                                                                                                                                                      | ![]()                                     |
| 28              | Acetone + IPA Clean (N2 dry) | <p>Cleaning Agent: Acetone then IPA<br>Ultra-Sonication: false</p>                                                                               | Squirt with Acetone, then IPA, then dry the surface with the N2 gun.                                                                                                                                                 | ![]()                                     |
| 29              | HMDS Vapor Prime             | <p>Deposited Monolayer: HMDS<br>Layer Thickness: 5 Å</p>                                                                                         | <p>Not Using an actual vapor primer.<br><br>Spin @ 3000 rpm for 20 s<br>bake at 100C for 20 s</p>                                                                                                                    | ![]() |
| 30              | Spin Resist                  | <p>Resist: AZ P4210<br>Resist Type: Positive<br>Spin Speed: 4000 rpm<br>Spin Time: 30 secs</p>                                                   |                                                                                                                                                                                                                      |                                                                                                                                                                                                                                                                                                                                                                                                                                                                                                                                                                                                                                                                                                                                                                                                                                                                                                                                                                                                                                                                                                                                                                                                                                                                                                                                                                                                                                                                                                                                                                                                                                                                                                                                                                                                                                                                                                                                                                                                                                                                                |
| 31              | Bake                         | <p>Bake Temperature: 100 °C<br>Bake Time: 90 secs</p>                                                                                            |                                                                                                                                                                                                                      |                                                                                                                                                                                                                                                                                                                                                                                                                                                                                                                                                                                                                                                                                                                                                                                                                                                                                                                                                                                                                                                                                                                                                                                                                                                                                                                                                                                                                                                                                                                                                                                                                                                                                                                                                                                                                                                                                                                                                                                                                                                                                |
| 32              | Stepper Lithography          | Exposure time: 8 secs                                                                                                                            | Pattern 3 - Defining Al contact areas                                                                                                                                                                                |                                                                                                                                                                                                                                                                                                                                                                                                                                                                                                                                                                                                                                                                                                                                                                                                                                                                                                                                                                                                                                                                                                                                                                                                                                                                                                                                                                                                                                                                                                                                                                                                                                                                                                                                                                                                                                                                                                                                                                                                                                                                                |
| 33              | Develop                      | <p>Developer: AZ 400K 3:1 (DI water : developer)<br>Develop Time: 60 secs<br>Develop Temperature: 25 °C</p>                                      | Develop time may vary, use current stable patterning process. Modulate exposure time and develop time as needed to achieve good pattern resolution.                                                                  |                                                                                                                                                                                                                                                                                                                                                                                                                                                                                                                                                                                                                                                                                                                                                                                                                                                                                                                                                                                                                                                                                                                                                                                                                                                                                                                                                                                                                                                                                                                                                                                                                                                                                                                                                                                                                                                                                                                                                                                                                                                                                |
| 34              | Wet-Etch                     | <p>Etch Time: 20 secs<br>Etching Agent(s): 6:1 BOE (HF)</p>                                                                                      |                                                                                                                                                                                                                      |                                                                                                                                                                                                                                                                                                                                                                                                                                                                                                                                                                                                                                                                                                                                                                                                                                                                                                                                                                                                                                                                                                                                                                                                                                                                                                                                                                                                                                                                                                                                                                                                                                                                                                                                                                                                                                                                                                                                                                                                                                                                                |
| 35              | Wet Strip Resist             | Stripping Agent(s): Acetone then IPA                                                                                                             | Squirt with acetone, then IPA, then dry with N2 gun                                                                                                                                                                  |                                                                                                                                                                                                                                                                                                                                                                                                                                                                                                                                                                                                                                                                                                                                                                                                                                                                                                                                                                                                                                                                                                                                                                                                                                                                                                                                                                                                                                                                                                                                                                                                                                                                                                                                                                                                                                                                                                                                                                                                                                                                                |
| 36              | Thermal Evaporation          | Film thickness: 500 nm                                                                                                                           | Alternatively sputtering can be used depending on available lab tooling.                                                                                                                                             |                                                                                                                                                                                                                                                                                                                                                                                                                                                                                                                                                                                                                                                                                                                                                                                                                                                                                                                                                                                                                                                                                                                                                                                                                                                                                                                                                                                                                                                                                                                                                                                                                                                                                                                                                                                                                                                                                                                                                                                                                                                                                |
| 37              | Acetone + IPA Clean (N2 dry) | <p>Cleaning Agent: Acetone then IPA<br>Ultra-Sonication: false</p>                                                                               | Squirt with Acetone, then IPA, then dry the surface with the N2 gun.                                                                                                                                                 |                                                                                                                                                                                                                                                                                                                                                                                                                                                                                                                                                                                                                                                                                                                                                                                                                                                                                                                                                                                                                                                                                                                                                                                                                                                                                                                                                                                                                                                                                                                                                                                                                                                                                                                                                                                                                                                                                                                                                                                                                                                                                |
| 38              | Spin Resist                  | <p>Resist: AZ P4210<br>Resist Type: Positive<br>Spin Speed: 4000 rpm<br>Spin Time: 30 secs</p>                                                   |                                                                                                                                                                                                                      |                                                                                                                                                                                                                                                                                                                                                                                                                                                                                                                                                                                                                                                                                                                                                                                                                                                                                                                                                                                                                                                                                                                                                                                                                                                                                                                                                                                                                                                                                                                                                                                                                                                                                                                                                                                                                                                                                                                                                                                                                                                                                |
| 39              | Bake                         | <p>Bake Temperature: 100 °C<br>Bake Time: 90 secs</p>                                                                                            |                                                                                                                                                                                                                      |                                                                                                                                                                                                                                                                                                                                                                                                                                                                                                                                                                                                                                                                                                                                                                                                                                                                                                                                                                                                                                                                                                                                                                                                                                                                                                                                                                                                                                                                                                                                                                                                                                                                                                                                                                                                                                                                                                                                                                                                                                                                                |
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

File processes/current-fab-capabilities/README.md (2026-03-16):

---
description: Last Updated March 2026
---

# ✨ Self Aligned NMOS

* 952 Transistors per Chip
* 94% Yield
* 1.26V Threshold Voltage
* 5 um gate length

<figure><figcaption></figcaption></figure>

<figure><figcaption></figcaption></figure>

<figure><figcaption></figcaption></figure>

<figure><figcaption></figcaption></figure>

<figure><figcaption></figcaption></figure>

Process in Fabublox:

{% embed url="https://www.fabublox.com/process-editor/f52fe668-594d-4a94-bfb1-b1e3ce845f38" %}

| Step #          | Step Name                    | Parameters                                                                                                                                       | Comments                                                                                                                                                                                                             | Layer Stacks
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

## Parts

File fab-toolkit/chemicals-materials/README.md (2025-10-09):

---
hidden: true
---

# ⚗️ Chemicals / Materials

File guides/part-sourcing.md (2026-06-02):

---
description: >-
  Strategies for sourcing parts effectively, and a constantly updated list of
  part suppliers
layout:
  width: default
  title:
    visible: true
  description:
    visible: true
  tableOfContents:
    visible: true
  outline:
    visible: true
  pagination:
    visible: false
  metadata:
    visible: true
  tags:
    visible: true
  actions:
    visible: true
---

# Part Sourcing

## :woman\_running:We like making hardware, fast :man\_running:

##

### The Way we Source Parts

<details>

<summary>Use ChatGPT to Source Parts for You</summary>

* With Bing feature, you ask "source \_\_\_ for me" and add other details:
  * "prioritize parts with low lead times"
  * "inexpensive" or "hobby level"
  * "i liked this one you found, find me more of those"

</details>

<details>

<summary>Find the Part on Amazon</summary>

* Nothing is better than prime shipping
* If you found a part on a manufacturer's website, look up that exact part
* If you cannot find it, try searching for the manufacturer's amazon page
  * They normally have one

</details>

<details>

<summary>Avoid "Contact us for a Quote" at all times</summary>

* We try our best to not support companies that do this. If you ever start a company in the future, put a "buy now" button please.
* Long lead times, wasted time talking to someone, different prices if you are a university, company, individual, they try to package you in with expensive software, etc.

</details>

<details>

<summary>If you don't know which part to buy, use ChatGPT</summary>

* "what else are these parts called? anything else I could use instead"
* "I am trying to find a part that does X, Y, and Z, but I don't know what its called"
* "I am trying to attach \_\_\_ to \_\_\_\_, what can i use?"

</details>

<details>

<summary>As a last resort, you can contact manufacturers</summary>

Some teams, such as Thorlabs, Kurt Lesker, Filmtronics, are very knowledgable and can help bridge the gap of understanding. You can describe to them your situation, send them links of the parts you were considering, and ask them for their advice. Do this sooner rather than later - they take multiple days to respond.

</details>

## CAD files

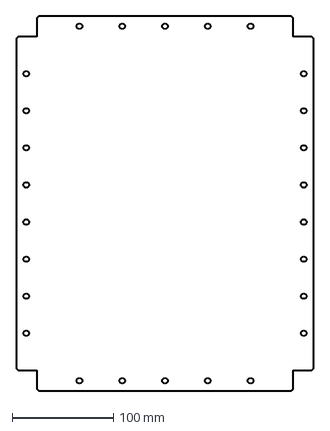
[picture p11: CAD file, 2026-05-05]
.gitbook/assets/Structure - Top Plate.dxf
294.6 x 370.8 mm

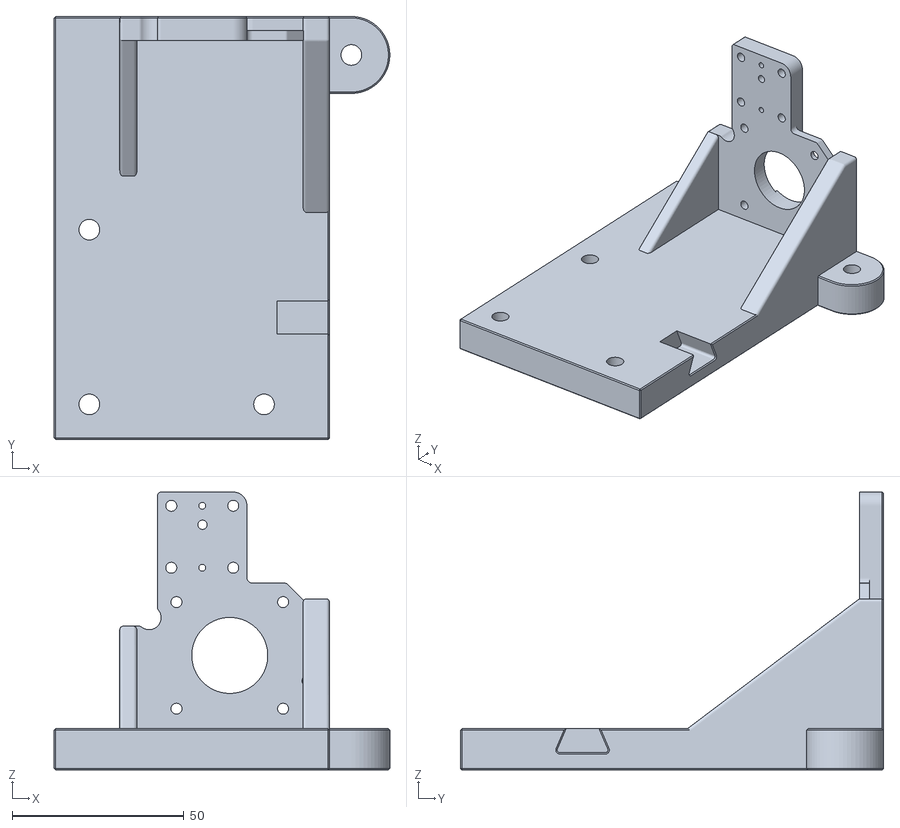
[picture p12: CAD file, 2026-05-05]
.gitbook/assets/Nanopositioner Mount - MotorMount_KM_2 (1).stl
97.6 x 123.0 x 80.8

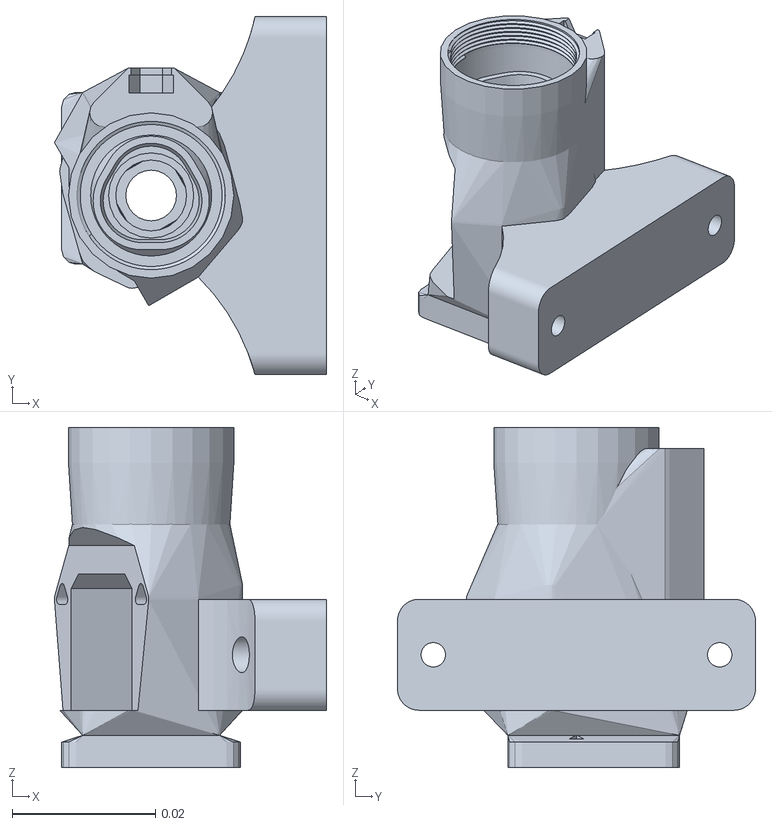
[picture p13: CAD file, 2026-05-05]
.gitbook/assets/optics_picamera2_rms_f50d13_beamsplitter_delta - Part 1.stl
0.038 x 0.05 x 0.0475

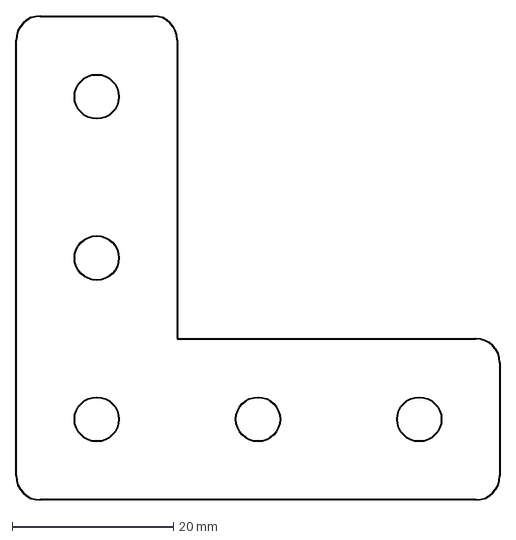
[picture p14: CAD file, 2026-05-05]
.gitbook/assets/Structure - Gusset.dxf
60.0 x 60.0 mm

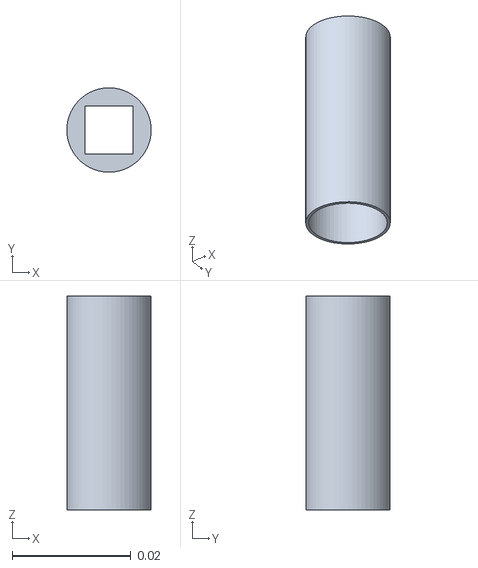
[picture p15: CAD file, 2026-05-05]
.gitbook/assets/transmission.stl
0.0142 x 0.0142 x 0.036

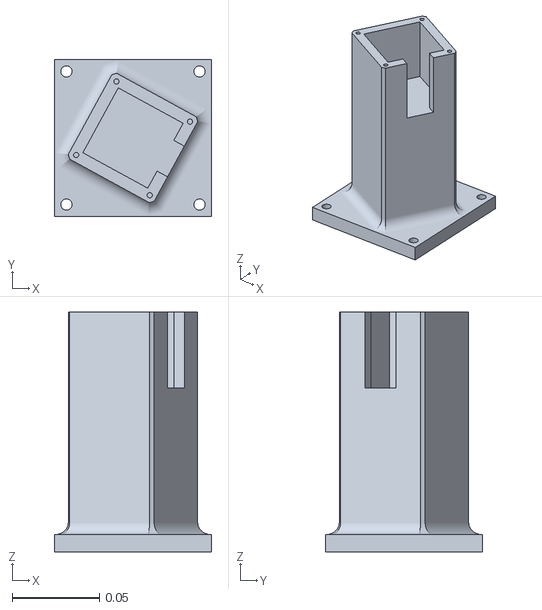
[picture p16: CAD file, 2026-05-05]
.gitbook/assets/mount_carousel.stl
0.09 x 0.09 x 0.137

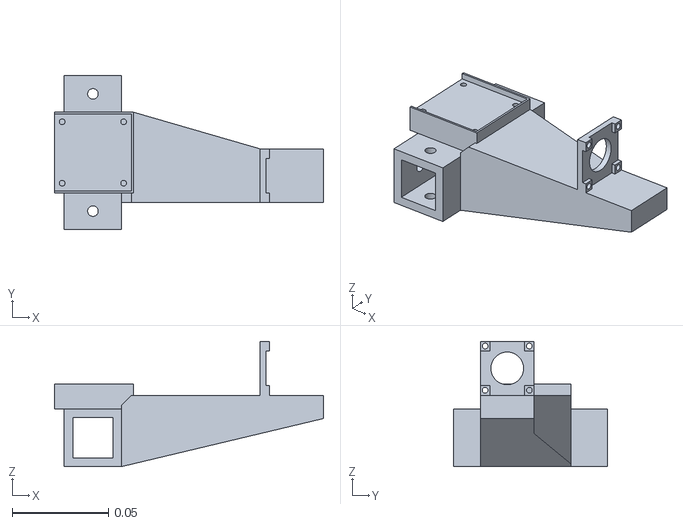
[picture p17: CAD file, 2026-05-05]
.gitbook/assets/system_mount.stl
0.14 x 0.08 x 0.0651

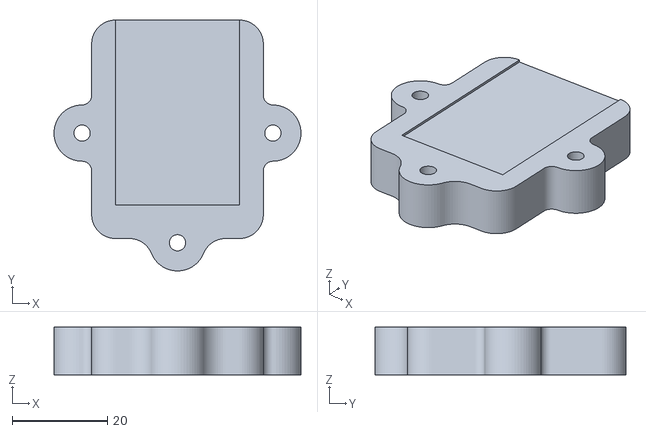
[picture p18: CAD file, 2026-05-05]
.gitbook/assets/Mounts - Slide Mount.stl
51.8 x 52.6 x 10.0

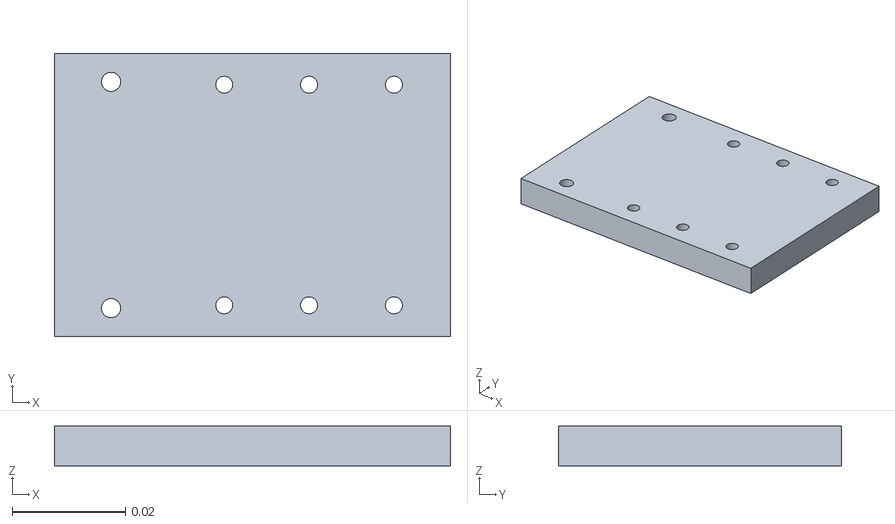
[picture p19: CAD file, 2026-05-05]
.gitbook/assets/link_part.stl
0.07 x 0.05 x 0.007

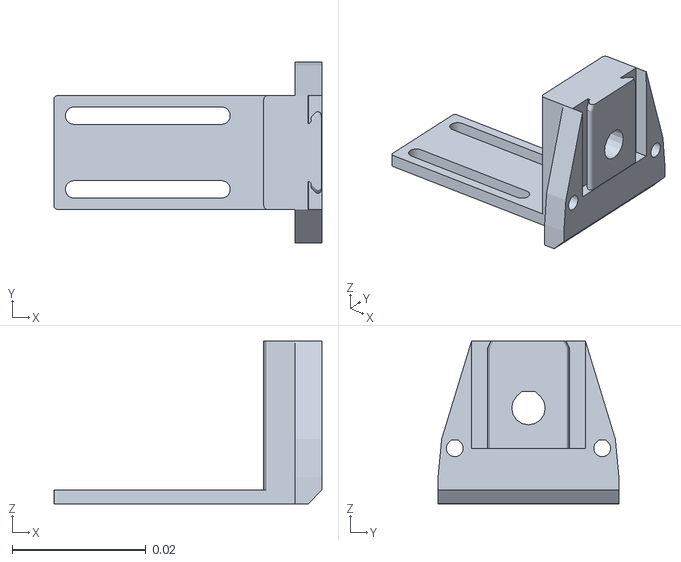
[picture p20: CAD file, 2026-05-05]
.gitbook/assets/reflection_illuminator_LED_star - Part 2.stl
0.04 x 0.027 x 0.0243

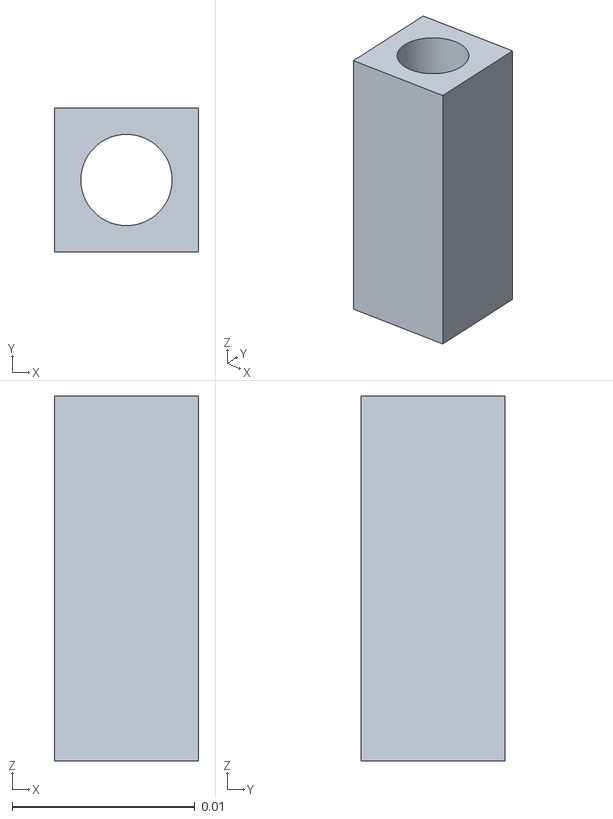
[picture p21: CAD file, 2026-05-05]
.gitbook/assets/square_motor.stl
0.0079 x 0.0079 x 0.02

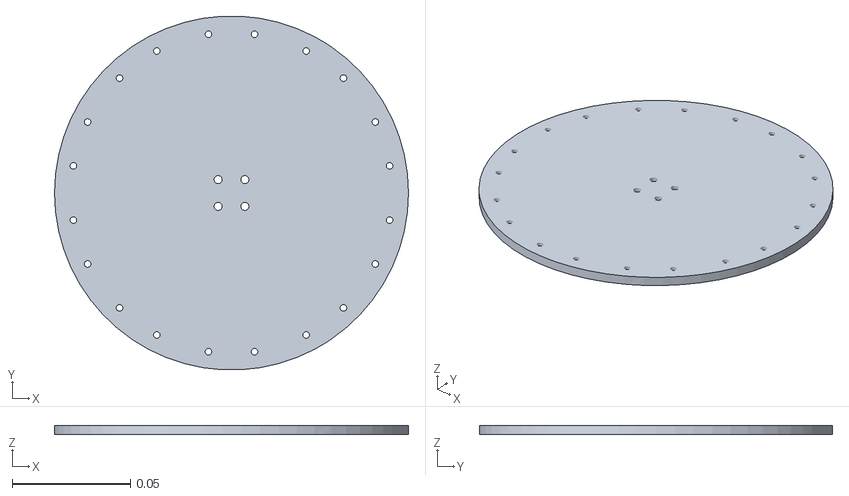
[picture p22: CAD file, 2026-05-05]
.gitbook/assets/platform.stl
0.15 x 0.15 x 0.004

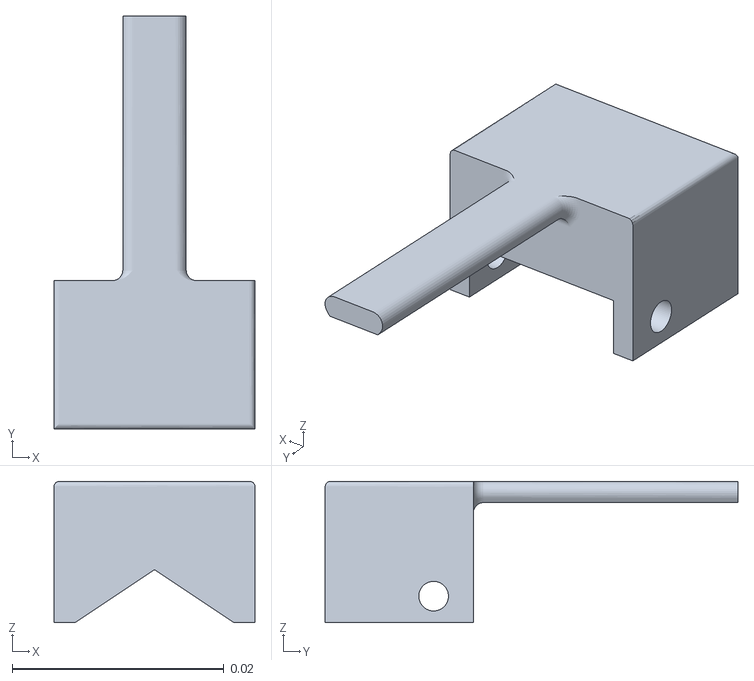
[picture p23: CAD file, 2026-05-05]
.gitbook/assets/push_part.stl
0.019 x 0.039 x 0.0133

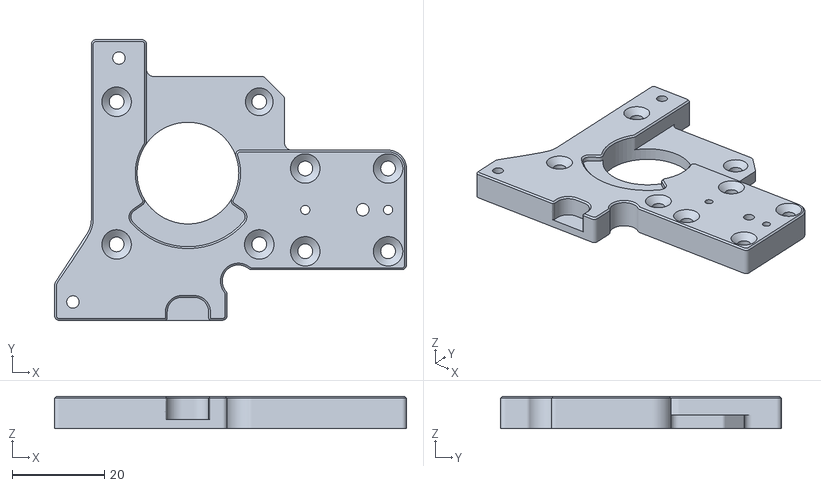
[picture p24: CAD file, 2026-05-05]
.gitbook/assets/Nanopositioner Mount - MotorMount_KM.stl
76.5 x 61.0 x 7.00

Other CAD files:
.gitbook/assets/microscope_holder.stl
.gitbook/assets/Structure - Base Plate.dxf
.gitbook/assets/Nanopositioner Mount - MotorMount_KM_1.stl
.gitbook/assets/mount_linear.stl
.gitbook/assets/Mounts - Microscope Ext. Bracket.stl
.gitbook/assets/chip_holder.stl
.gitbook/assets/picamera_2_cover.stl
.gitbook/assets/reflection_illuminator_LED_star - Part 1.stl

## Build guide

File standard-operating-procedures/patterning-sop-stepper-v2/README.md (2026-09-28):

---
layout:
  width: default
  title:
    visible: true
  description:
    visible: true
  tableOfContents:
    visible: true
  outline:
    visible: true
  pagination:
    visible: false
  metadata:
    visible: true
  tags:
    visible: true
  actions:
    visible: true
  anchors:
    visible: true
---

# Patterning SOP - Stepper V2

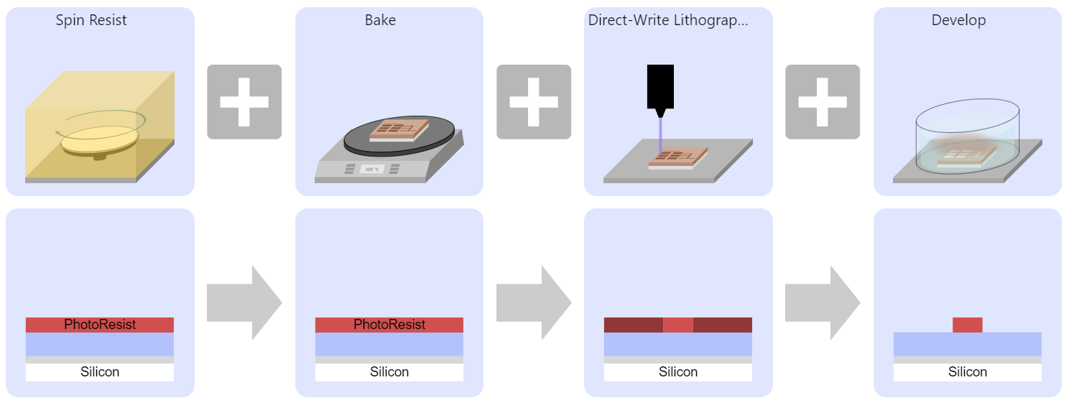
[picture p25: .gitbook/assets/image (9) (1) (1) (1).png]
<figure><figcaption><p>Generic Patterning Sequence</p></figcaption></figure>

## Parameters

<table><thead><tr><th width="262"></th><th width="116"></th><th width="213"></th><th></th></tr></thead><tbody><tr><td>HMDS Prebake Temperature</td><td>100°C</td><td>Resist Bake Temperature</td><td>100°C</td></tr><tr><td>HMDS Prebake Time</td><td>60s</td><td>Resist Bake Time</td><td>90s</td></tr><tr><td>HMDS Amount (Drops)</td><td>2</td><td>Exposure Pattern</td><td>link</td></tr><tr><td>HMDS Spin Speed</td><td>4000 rpm</td><td>Exposure Source</td><td>Stepper V2</td></tr><tr><td>HMDS Spin Time</td><td>20s</td><td>Exposure Time</td><td>5s</td></tr><tr><td>HMDS Bake Temperature</td><td>100°C</td><td>Exposure Dose</td><td></td></tr><tr><td>HMDS Bake Time</td><td>20s</td><td>Developer Type</td><td>AZ-400K</td></tr><tr><td>Resist Amount</td><td>2 drops</td><td>Develop Time</td><td>60s</td></tr><tr><td>Resist Spin Speed</td><td>4000 rpm</td><td>Developer Temperature</td><td>20°C</td></tr><tr><td>Resist Spin Time</td><td>30s</td><td></td><td></td></tr></tbody></table>

#### For More Detailed Process Parameters:

[Patterning Process Sheet](https://docs.google.com/spreadsheets/d/1JrOyISOwiZrRkdBT3utiHOze-yCluFcrFgd6_dhLPMw/edit#gid=38181110)

***

## Purpose

Patterning is the core of any micro/nanofabrication process, as it is used to mask etch and deposit steps. First we spin coat photoresist to deposit a thin layer. Then we use our maskless lithography stepper to expose our pattern in the resist with light. Finally we wash away the exposed region with developer. This leaves behind a resist pattern that is resistant to many types of acid and plasma etches. It can also be hard baked and used as a dielectric, or metal can be deposited on top of it for a lift off process. The procedure described here uses a positive resist, AZ-P4210, but negative resists also exist where unexposed areas become soluble.

See the appendix for useful resources about spin coating, our resist, and developer.

## Safety

* Harm to your eyes/eyesight is possible if you do not wear the right protective equipment. To shield your eyes from harmful UV-rays, everyone working with or near the stepper should wear UV-blocking goggles/glasses.
* HMDS is a toxic, volatile chemical that should only be used in the fume hood.
* Photoresist, while not as bad as HMDS, contains some nasty solvents and should be cleaned with acetone if it gets on anything other than chips and the spin coater.
* AZ-400K developer is a strong base containing KOH. Use the appropriate precautions for working with bases. Only agitate the developer inside the fume hood to reduce the chance of droplets.

***

## Tools

1. [Spin Coater](https://docs.google.com/document/d/16tg5COz3QADQcWTJfgbuTBRsJrYIF2IFitKL2VLnr3I/edit?usp=sharing)
2. [Hot Plate](https://docs.google.com/document/d/14IZRb_CLO6zwDDNvO9dSkzYD5jisfbr-6na2exCk-T0/edit?usp=sharing)
3. Flashlight Jig or Maskless Lithography Stepper

## Materials

1. [Hexamethyldisilazane (HMDS) adhesion promoter](https://docs.google.com/document/d/1Wtk8l1dXzwlhdUSQaCBSIJ00-sB0tanP0AOklIOY0Ik/edit?usp=sharing)
2. AZ-4210 positive photoresist ([specsheet](https://www.microchemicals.com/micro/tds_az_p4000_series.pdf))
3. AZ-400K Developer
4. Acetone
5. Isopropanol
6. Deionized water
7. Evaporating dish

## Photoresist Alternative

UV-curable 3D printing resin can serve as an effective substitute for conventional photoresist. It is inexpensive (approximately $15 on Amazon), easy to obtain, and generally less hazardous to handle.

Due to its relatively high viscosity, the resin should be spin-coated at lower rotational speeds. Viscosity varies by brand and formulation, typically ranging from 150 to 1500 cP (mPa·s). In our trials, spin speeds between 1000 and 2000 rpm produced uniform coatings.

When exposed using the default blue LED on the litho-stepper projector at maximum current, the resin required approximately 30–60 seconds to cure. The longer exposure time compared to photoresist is likely due to the greater film thickness. This value may vary depending on coating thickness and light intensity.

Development:\
Isopropyl alcohol (IPA) can be used as a substitute for standard photoresist developers or etchants. Complete removal can be challenging, so a combination of DI water rinse followed by IPA spray is recommended for best results.\
\
Figure 1: sample checkerboard patterns\
\
Figure 2: microscope close up (grey/black is UV resin, blue is wafer)\
<br>

***

## Procedure

### Preparation

1. If you have already claimed a chip number, and opened its specific chip view data sheet, record your patterning data into that sheet. If you have NOT claimed a chip number, and have NOT begun recording data in a chip specific sheet, open this [central chip count](https://docs.google.com/spreadsheets/d/1MrqtnkHcNr5hekHpQHusBZJG4nrdcxDz7Yg5Emn9BMQ/edit#gid=0) sheet, claim the next available chip number, open the blank chip view sheet for that specific chip number and record all subsequent process data into it.
2. [Cleave](https://docs.google.com/document/d/1UWZ_X2TpRqdOWOC8YGubfD7xW-dz4nRNzJk5c_mo4w0/edit?usp=sharing) the Si wafer into a \~1 cm x 1 cm square.
3. Dust off the wafer with the nitrogen gun

### Wafer Cleaning

1. In the fume hood, hold the wafer with tweezers over the sink.
2. Rinse the polished side of the wafer thoroughly with acetone, then isopropyl alcohol.
   1. The acetone leaves a residue that must be removed by the isopropyl alcohol rinse.
3. Blow the wafer dry with the nitrogen gun.
   1. Even when the wafer appears dry, there may still be moisture on the edges, so dry liberally.
4. Inspect with the naked eye and note any marks on the wafer.
   1. Marks present after cleaning are likely scratches that need to be documented so we observe their effect on the process.

### Spin Coat

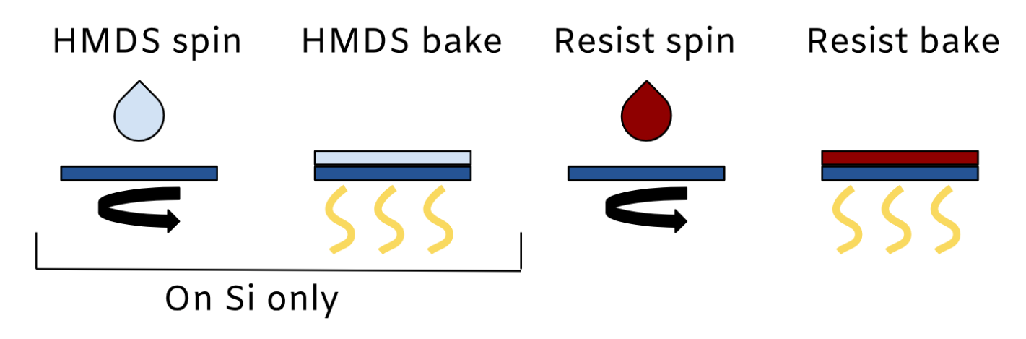
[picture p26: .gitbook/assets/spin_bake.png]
<figure><figcaption></figcaption></figure>

5. See the [Vacuum Spin Coater SOP](https://hacker-fab.gitbook.io/hacker-fab-space/standard-operating-procedures/patterning-sop-stepper-v2/vacuum-spin-coater-sop). Remember to pipette an appropriate amount, close the lid, and turn on the vacuum.
6. If previous steps required cleaning with solvents, pre-bake the wafer to dehydrate the surface.
7. If patterning on silicon or glass, spin coat 2-3 drops of HMDS. Otherwise skip to 7.
   1. Choose Time and RPM from [patterning data sheet](https://docs.google.com/spreadsheets/d/1T9-kXXxdD9c6KZh_iy1LGt8I8wGlmeVlIZmvBrkVQ2g/edit#gid=0)
8. HMDS bake on the hot plate at 100°C for 60 seconds.
9. Spin coat as much photoresist as needed to mostly cover the chip, normally 3-4 drops.
   1. Choose Time and RPM from [patterning data sheet](https://docs.google.com/spreadsheets/d/1T9-kXXxdD9c6KZh_iy1LGt8I8wGlmeVlIZmvBrkVQ2g/edit#gid=0)
   2.  If chip is having trouble sticking on o-ring either: try pressing top of chip while vacuum is on with some pressure to make a better seal (use plastic tweezers)

       
   3. Or, take o-ring off and clean then re-install.
10. Soft bake on the hot plate at 100°C for 90 seconds.

## Stepper Setup

1. Power: Check that the projector, stage, and vacuum pump are all plugged in.
2. Plug the HDMI cable for the projector, the USB camera cable, and the Arduino + CNC Shield USB into your computer.
3. Set up the projector as an extended screen on your computer’s display settings (Win+P on Windows).
4.  Prepare your exposure, red align, and UV focus patterns.

    1. Your exposure pattern should be pure blue in the areas you want exposed, and black elsewhere. Include alignment marks for the next layer.
    2. Your red align image should be completely pure red except for alignment marks that match the previous layer.
    3. Your UV focus pattern should be completely black except for blue focus marks. Ideally these should be in a region that gets fully exposed. You may also use grayscale to avoid unintentional exposure.

    Note: If your pattern images have extraneous color components, the GUI has options to enable/disable different color channels for the red focus, UV focus, and exposure pattern. Use these at your convenience.
5. Set up the patterning GUI util script
   1. In the source or scripts folder, find and open config.py in your text editor of choice. If your GUI has an integrated camera implemented, set RUN\_WITH\_CAMERA to True. If your GUI uses a motorized stage, set RUN\_WITH\_STAGE to True.
   2. Run the python script called Lithographer.py. You can do this by opening a terminal and running the command "py -3.10 Lithographer.py". Make sure you have all dependencies installed as described in [Lithography Stepper V2 Build](../../fab-toolkit/patterning/lithography-stepper-v2-build-work-in-progress.md). If the program does not run, see [#troubleshooting](./#troubleshooting "mention").
   3. Move the black full-screen window to the projector (on windows, this is shift + win + L/R arrow)
   4. Use the three import thumbnails to select the desired images, these can be changed whenever. Make sure they are correct using the small previews.
   5. For more information about the software and its usage, click the "help" button at the bottom right of the GUI.
6. If you do not have an integrated GUI camera implemented and you are using the Flir Camera, open SpinView, select BlackFly S, and press the green play button. If you see horizontal bands across the live camera preview, follow the corresponding steps in [Troubleshooting](./#troubleshooting).
7. The GUI should appear similarly to below. If you do not see content on the camera preview yet, this is fine for now.

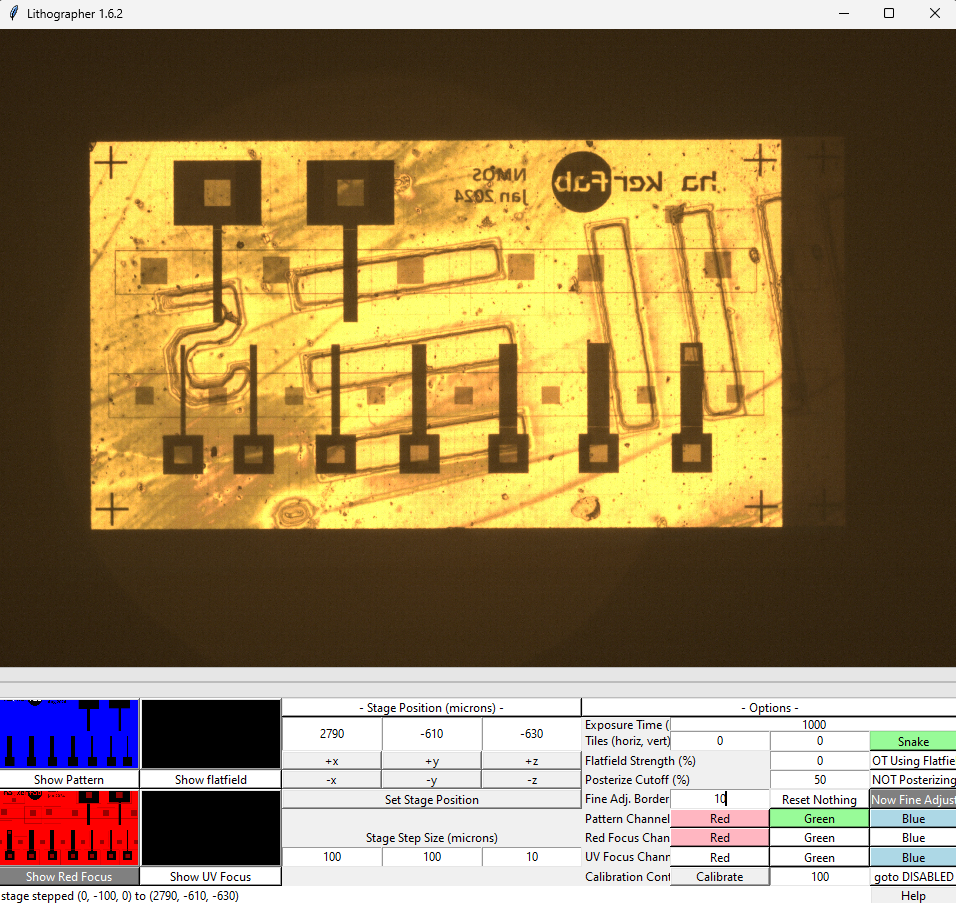
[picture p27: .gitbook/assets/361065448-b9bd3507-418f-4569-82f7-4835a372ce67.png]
<figure><figcaption></figcaption></figure>

### Expose Using Maskless Photolithography Stepper

If you're doing this for the first time, it is recommended to read through the full instructions before starting. You will need to move somewhat quickly because the stepper will begin to expose photoresist in about 1 minute.

1. Make sure the correct pattern is loaded in the Lithographer GUI. See step 4.4 in [#stepper-setup](./#stepper-setup "mention")

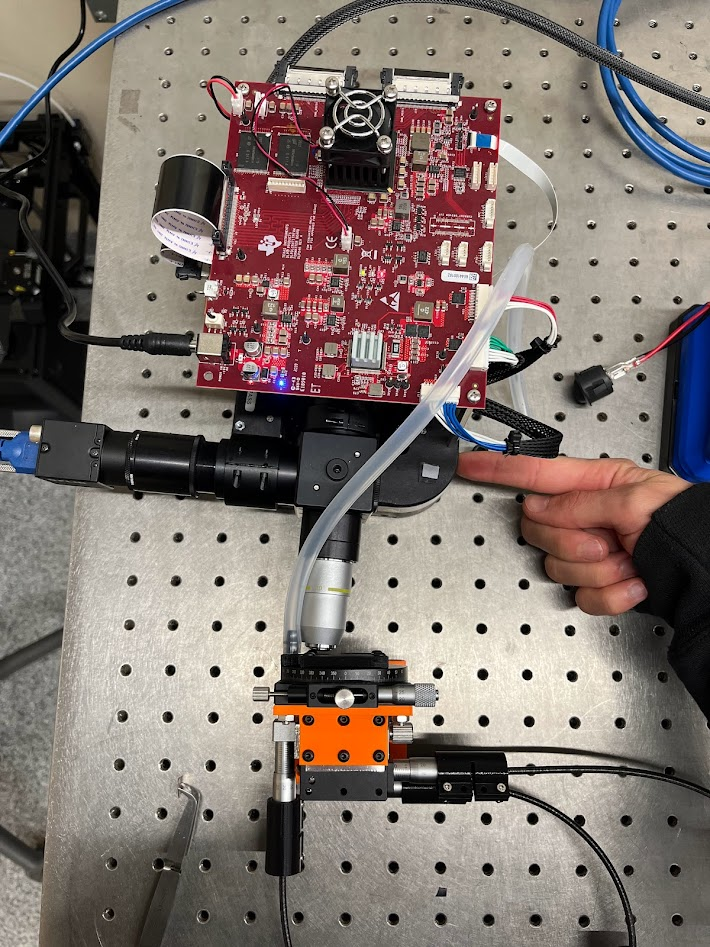
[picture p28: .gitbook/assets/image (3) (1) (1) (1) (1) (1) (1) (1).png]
<figure><figcaption></figcaption></figure>

2. LYFT and move the projector to the left, out of the way of the small hole in the chip holding jig.

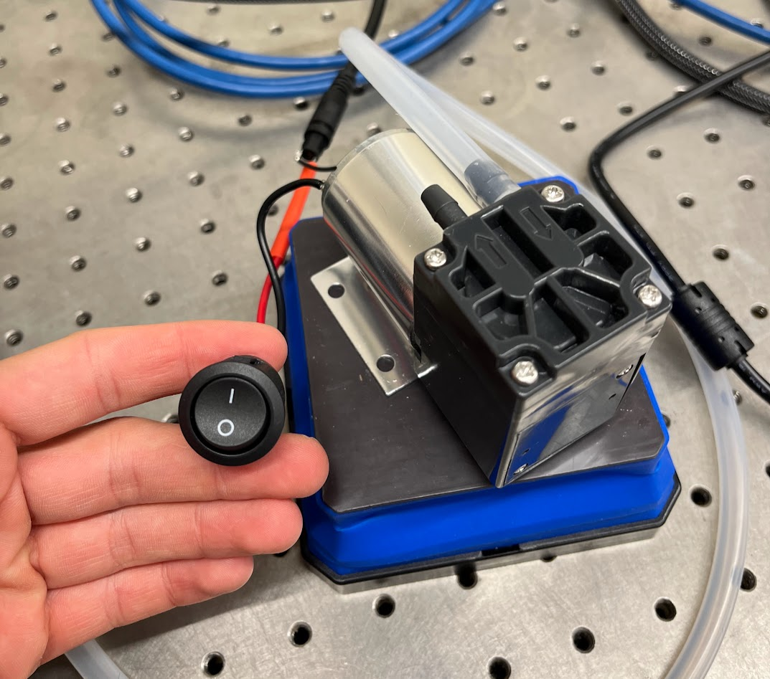
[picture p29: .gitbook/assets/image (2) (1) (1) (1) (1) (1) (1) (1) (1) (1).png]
<figure><figcaption></figcaption></figure>

3. Turn on the vacuum pump. Ensure vibrations are isolated from the rest of the stepper.

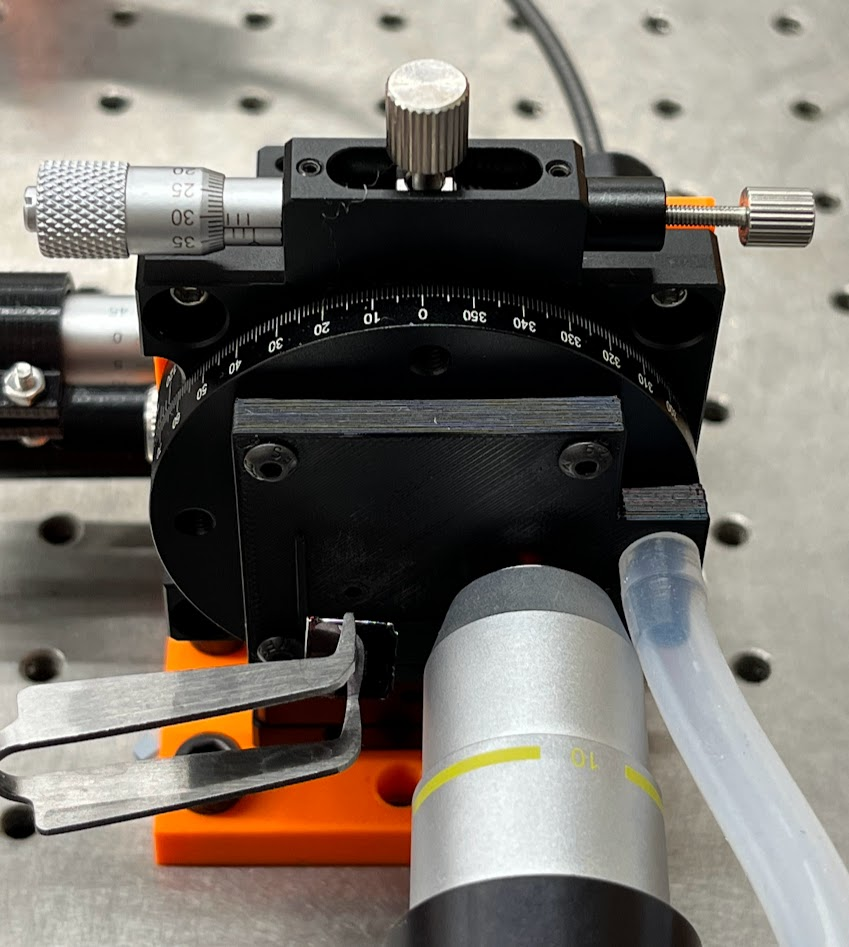
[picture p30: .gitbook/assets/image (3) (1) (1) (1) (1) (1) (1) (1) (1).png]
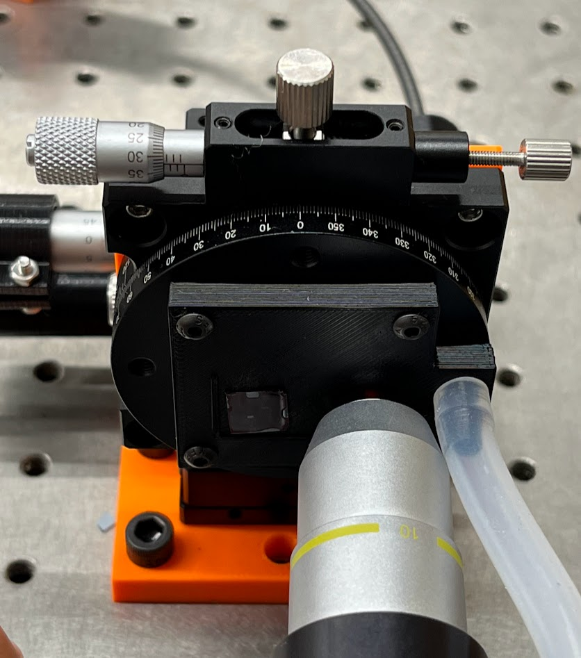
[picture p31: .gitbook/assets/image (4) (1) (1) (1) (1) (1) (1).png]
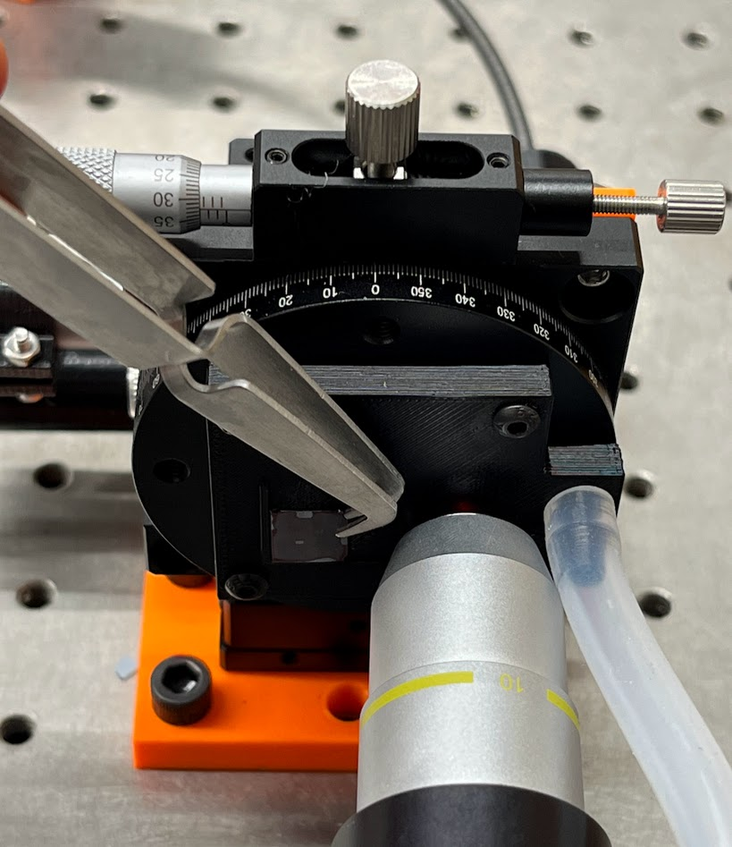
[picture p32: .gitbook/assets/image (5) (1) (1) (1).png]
  

4. Orient the chip over the hole with its squarest corner in the corner of the alignment jig. The vacuum will suck it against the jig. Push the chip into the corner. Doing this repeatably eliminates the need to adjust theta.

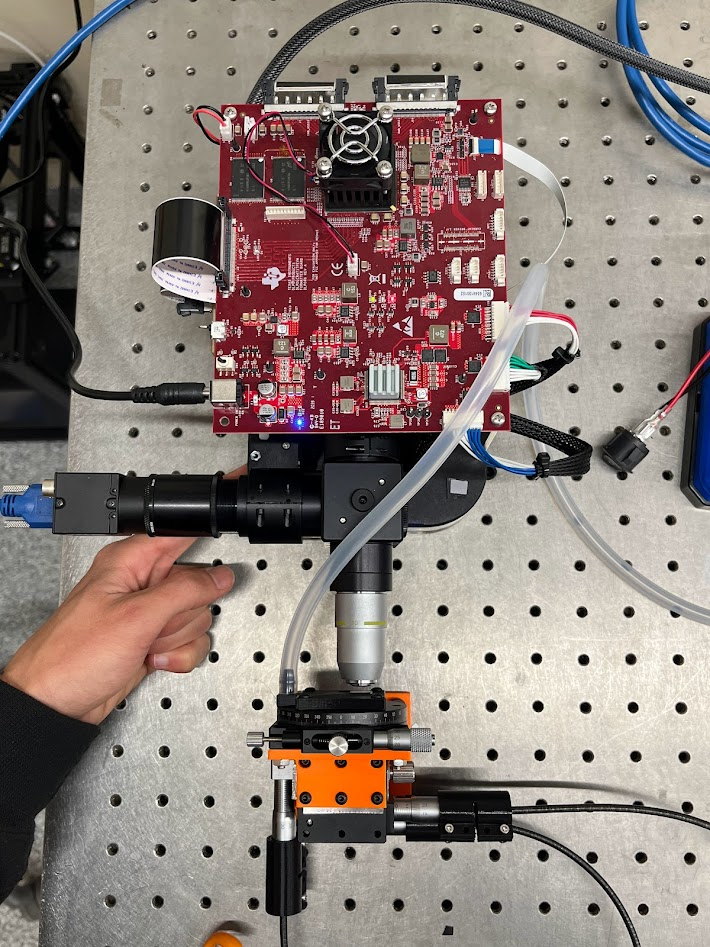
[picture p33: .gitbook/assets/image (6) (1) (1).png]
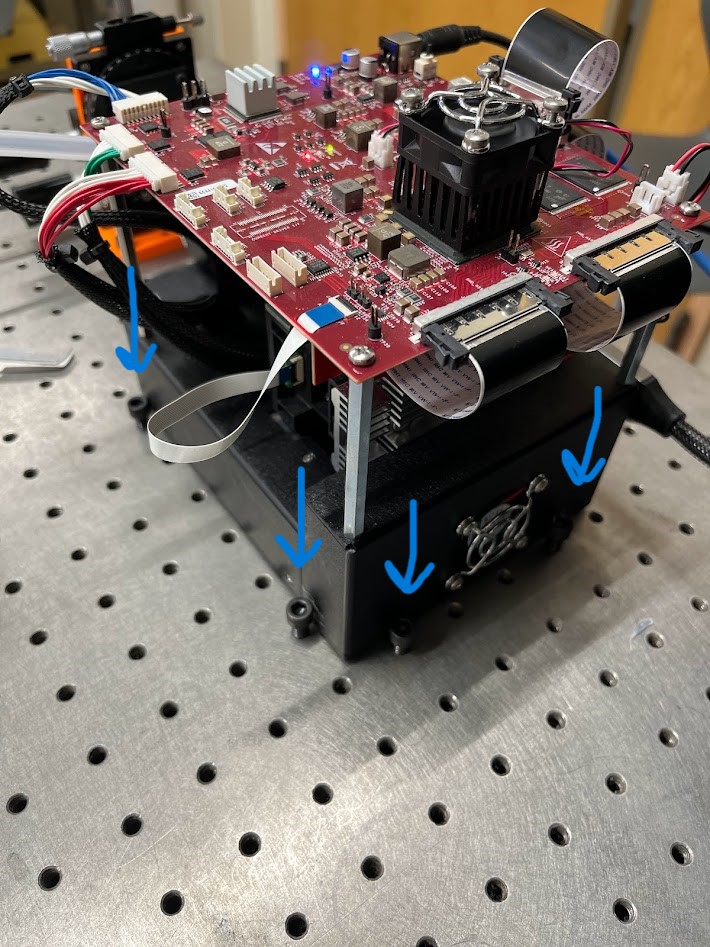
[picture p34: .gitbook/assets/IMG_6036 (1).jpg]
 

5. LYFT and move the projector back into place. Ensure it is touching all four bolts. Be careful about not scratching the chip.

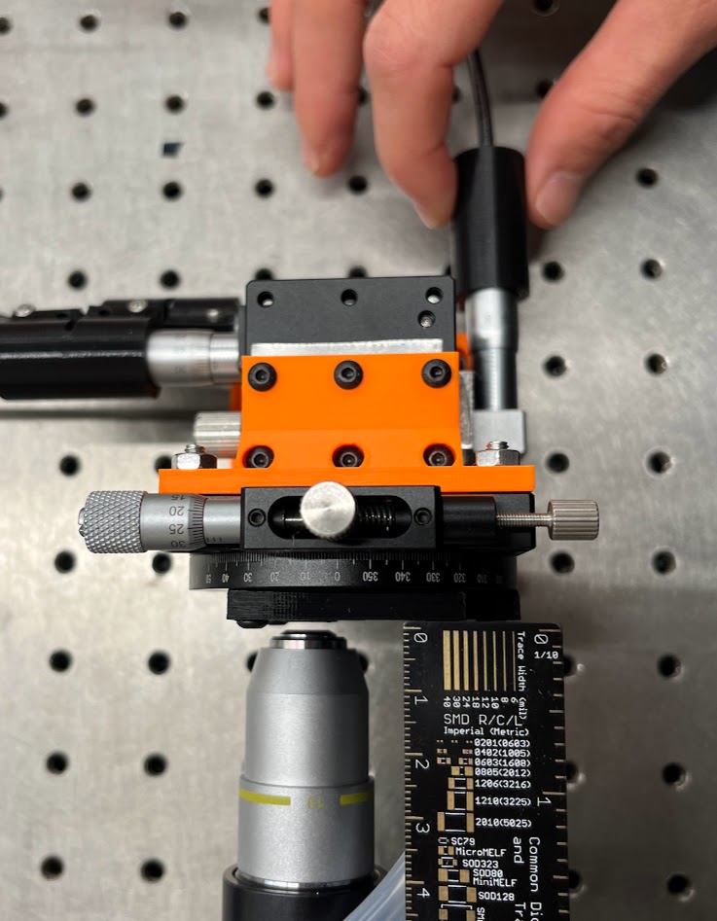
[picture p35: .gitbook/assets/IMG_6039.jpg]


6. Turn the Z knob on the stage or modify the GUI stage coordinates until the objective lens is \~2mm from the chip and the image on SpinView or the GUI is in focus.

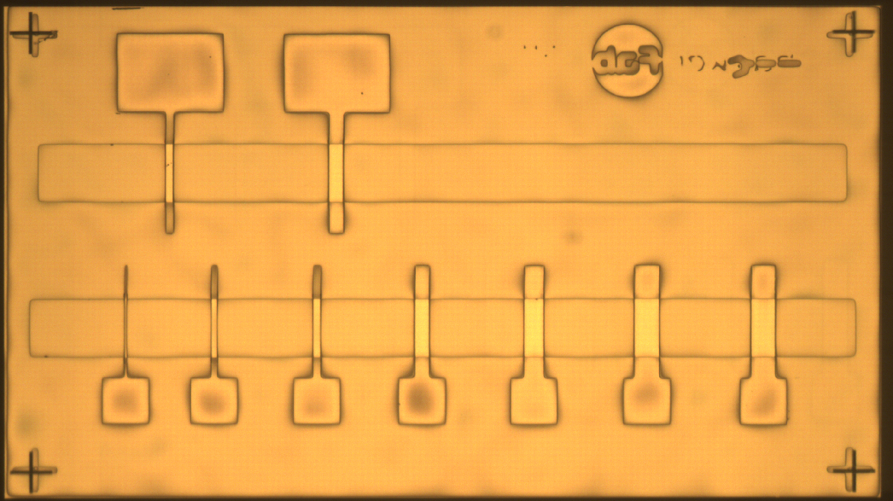
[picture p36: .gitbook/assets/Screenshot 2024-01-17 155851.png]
<figure><figcaption><p>A well aligned exposure. Note that the previous layer is slightly smaller than the proected pattern.</p></figcaption></figure>

7. Move the X and Y axes manually, or by using the GUI. One arbitrary "step" is approximately equal to 1 micron. To avoid straining the motors/stage, test small step sizes (i.e. 1) before trying larger ones (i.e. 10 or more). The minimum reliable step size is about 8-12 microns.
8. If this is your first layer, find an area with minimal contaminants, plan how many exposures you will do, and in which direction you will move. Otherwise, align to your previous layer using your pattern's alignment marks.
9. Once you're ready to expose, move the Z axis by -54 steps (fine-tune if necessary). This will switch from focusing in red to focusing in UV.
10. Set your exposure time to 8000 ms.

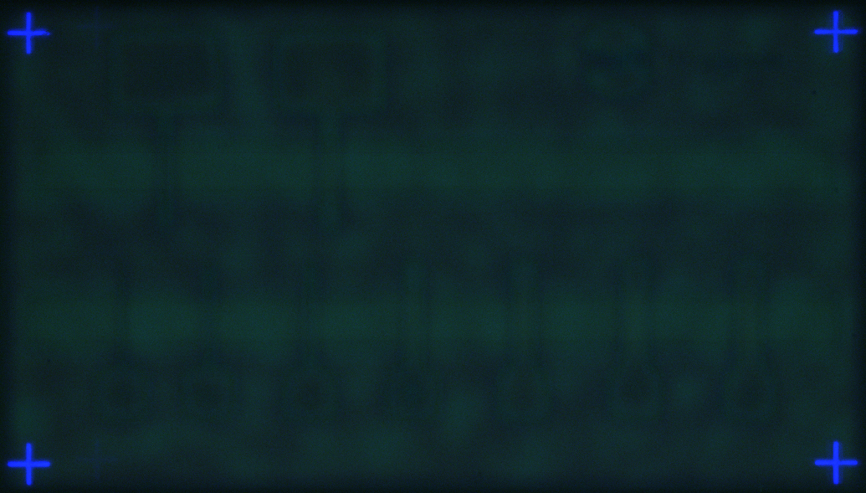
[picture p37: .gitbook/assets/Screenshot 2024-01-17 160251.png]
<figure><figcaption><p>Well-focused UV, ready to expose.</p></figcaption></figure>

12. Press show UV focus. You are now exposing the photoresist, so try to do this quickly. If necessary, make fine adjustments to the Z axis if any marks seem less in focus than others. The image above is well focused (all crosses look in focus).
13. Press the big red "Begin Patterning" button. Avoid bumping the table while you wait for the exposure to finish.
14. Press "Show Red Focus" and move in Z by +54 steps to switch back to red.
15. Move on to your next pattern and repeat. A good spacing between patterns is 580 steps in Y and 1080 steps in X (assuming one step per micron). This will allow you to easily find your next pattern. Take note of where you started, which direction you're moving, and how many exposures you've done so that you don't miss any patterns.
16. Once you're finished, press "Clear". Push the projector to the left again, and carefully hold your chip with tweezers while you turn off the vacuum.

## Develop

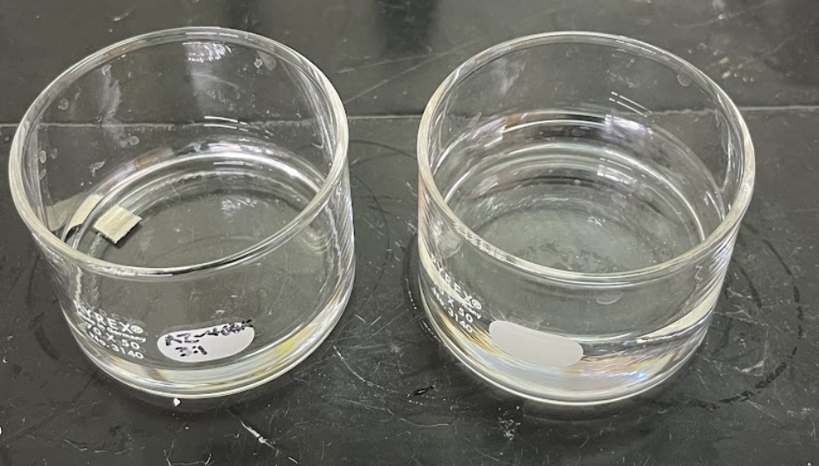
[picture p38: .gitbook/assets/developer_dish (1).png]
<figure><figcaption><p>Developer (Deionized water to AZ-400K 3:1) and DI water rinse.</p></figcaption></figure>

1. Refresh the developer if it has been out for more than 6 hours. Otherwise skip to step 2.
   1. Pour the used developer into the bottle labeled "developer waste"
   2. Rinse the evaporating dish with DI water.
   3. Pour about 30 mL of pre-diluted 3:1 AZ-400K developer solution into the evaporating dish labeled “AZ-400K 3:1”. For a sense of scale: in the dish above this should only be about 3mm tall of liquid (just enough to cover the surface of the chip)
   4. Fill another evaporating dish halfway with DI water.
2. Start the timer **at the same time as you drop the wafer into the developer**, photoresist side up.

<figure><figcaption><p>Agitate the developer</p></figcaption></figure>

5. **Agitate the chip in the developer solution with quick, small circular motions. Watch** [**this video**](https://drive.google.com/file/d/1C2APhZpUS7O2a-3hzmjMloyEuc7RCg1Z/view?usp=sharing) **for proper technique. This is crucial to getting a good pattern!**
6. 5 seconds before the end of the timer, pick up the chip and prepare to drop it into the water. The chip should **hit the water exactly at 0 seconds**. Rinse well for 10 seconds.
   1. Note that development time includes all the time that developer is touching the chip, not just during agitation
7. Dry off the chip with compressed air.

## Inspect

1. Look at the chip with your bare eyes to help build an intuition for the process.
2. Put the chip under the microscope. Connect to the camera with your laptop and take pictures of each developed pattern at 5x. If there are smaller interesting features or defects, you may take pictures at higher magnification or under dark field. Be aware that it's easy to get carried away with the microscope.
3. **If you want to measure the length of pitch in microns (μm) then you must use only the calibrated objective.**
   1. This calibration converts pixels of the camera to microns using a calibration slide from the manufacturer. If you use a different objective, the measurement will be inaccurate.
   2. After this is selected, measure the pitch or any other length using the line tool

<figure><figcaption><p>Measuring Microns with a 10x Objective</p></figcaption></figure>

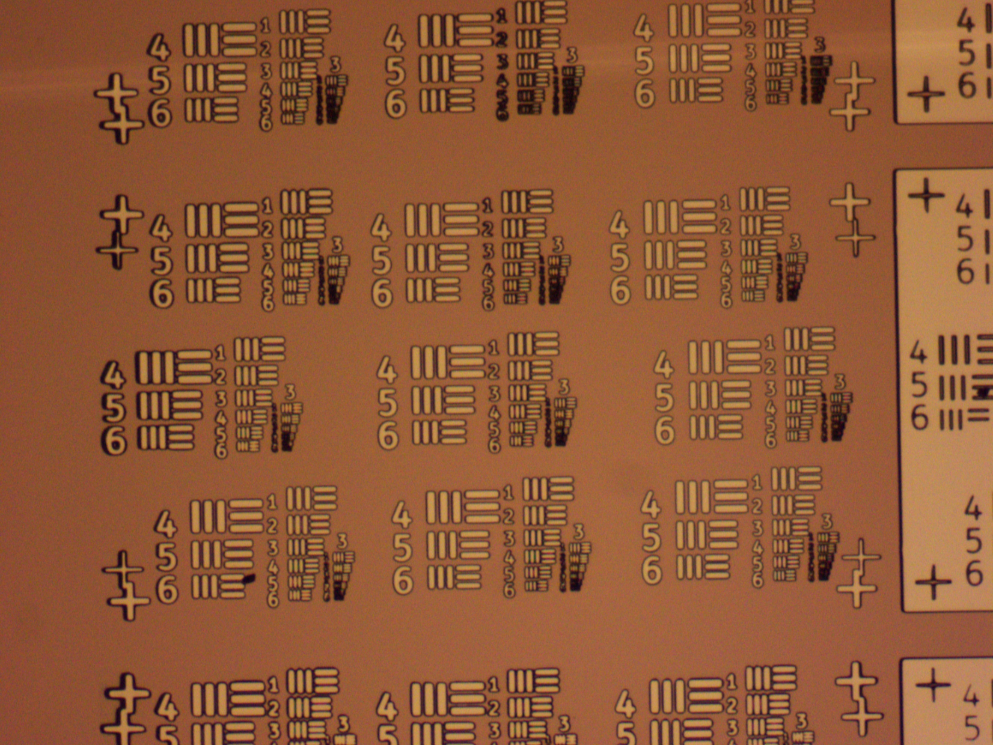
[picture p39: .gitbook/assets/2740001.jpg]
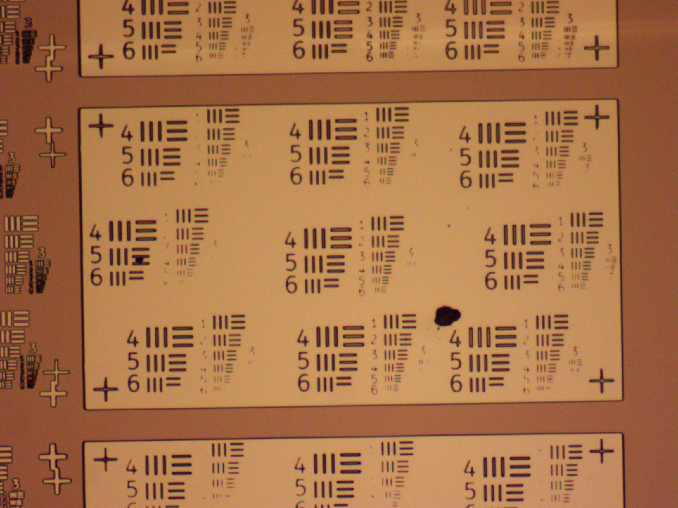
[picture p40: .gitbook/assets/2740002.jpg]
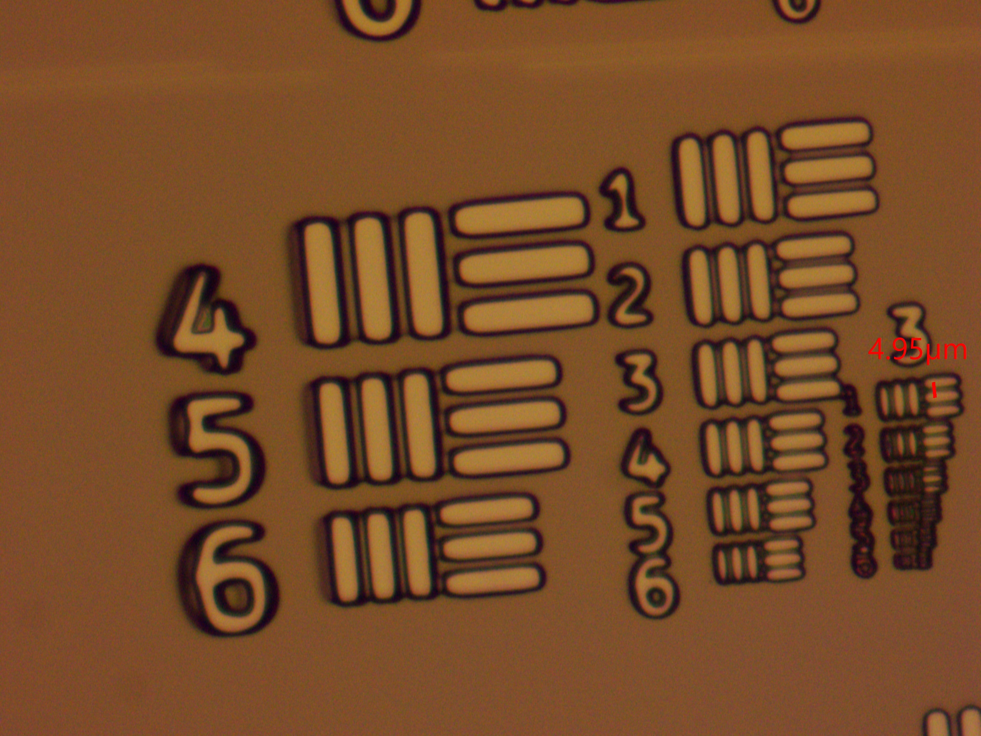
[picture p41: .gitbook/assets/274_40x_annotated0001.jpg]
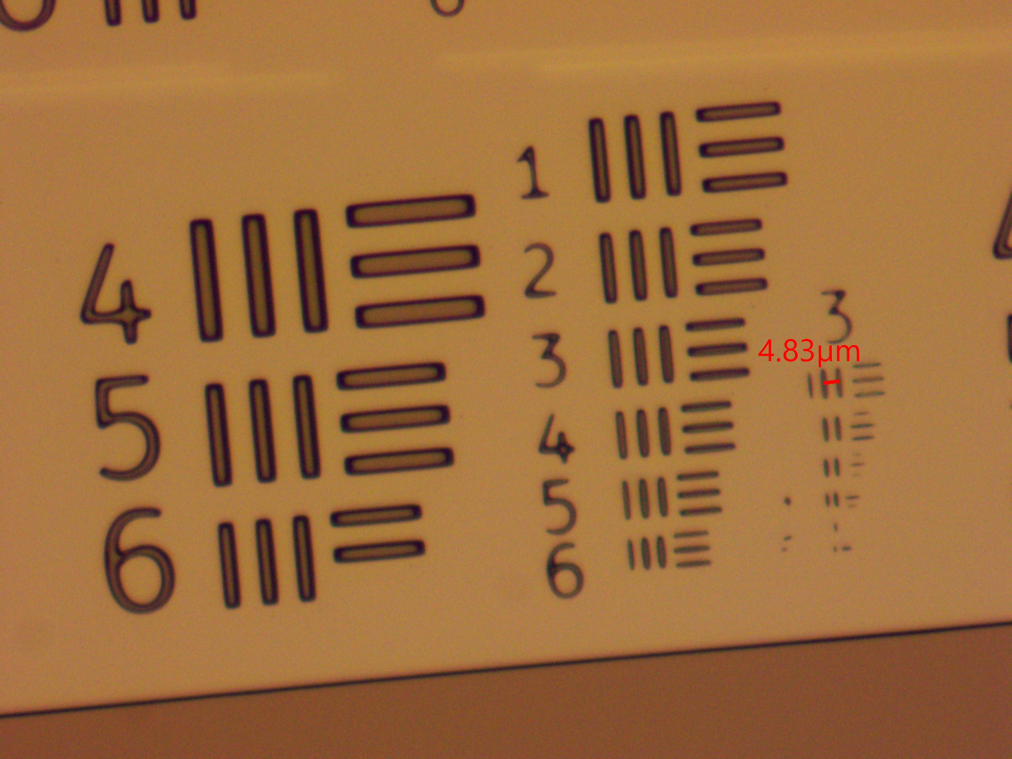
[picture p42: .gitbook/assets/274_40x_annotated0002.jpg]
   

4. In order to measure the developed pattern resolution, expose [this resolution test pattern](https://docs.google.com/presentation/d/16IsbOxES9O-imGjrv0Toe71-hkYhzWTv_O2MjYu2rck/edit?usp=sharing). The resolution is equal to the line pitch that is resolved in both light and dark field. Use AmScope to measure. The pitch is the distance between the center of two lines.
5. For each chip, batch save with the chip number as the first three characters in the file prefix. Do not change the folder. A script will upload to [drive](https://drive.google.com/drive/u/1/folders/1ySfcQiROhOYFecQzDvk9XBO2B2KqJLy6) every 5 min.
6. Paste a link to the folder in the last column of the chip sheet.
7. Put the chip away in a plastic box and label it with a serial number.

See below for examples of underexposure/development, overexposure/development, non-uniformity, and optical blurring.

<figure><figcaption><p>Inspection image demonstrating non-uniform exposure</p></figcaption></figure>

Right side: thicker lines and blurry edges. Left side: thin lines and sharp edges.

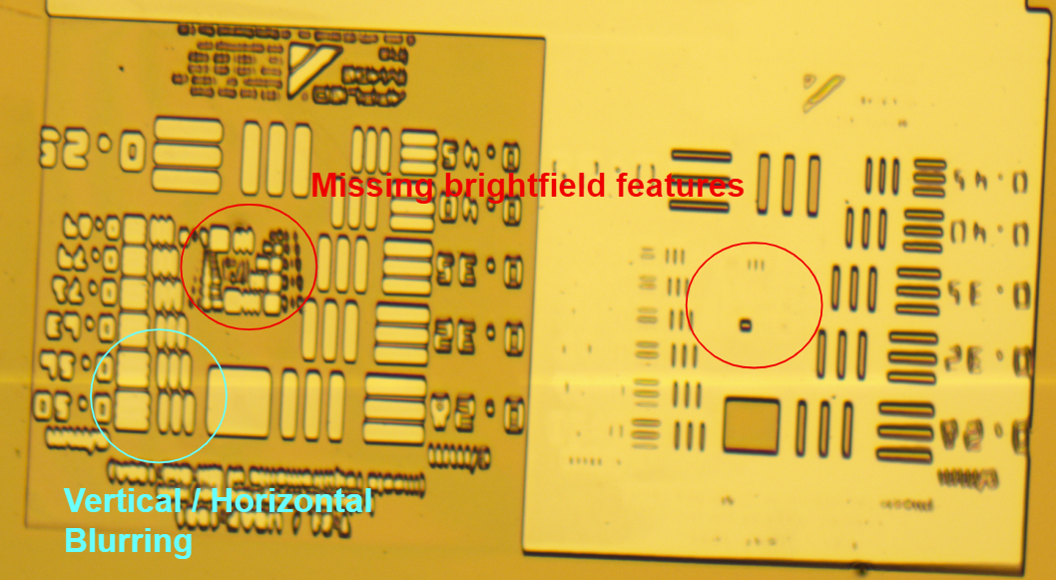
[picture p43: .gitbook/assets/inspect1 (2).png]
<figure><figcaption><p>Inspection image showing blurring effect from defocused stepper</p></figcaption></figure>

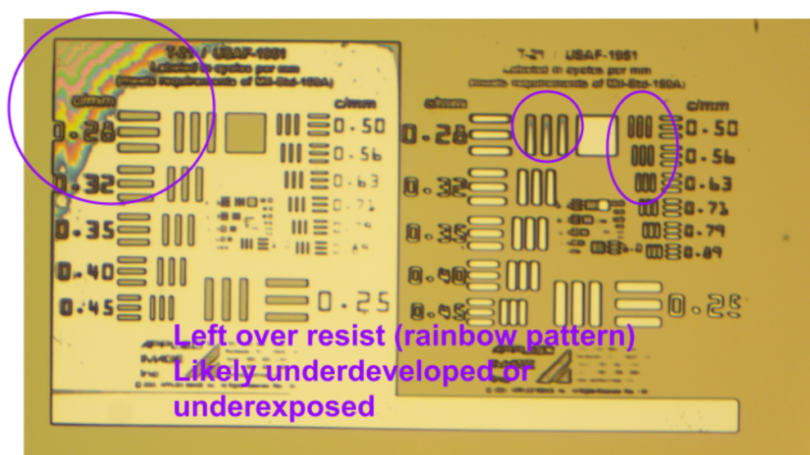
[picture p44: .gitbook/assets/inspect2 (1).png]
<figure><figcaption><p>Insprction image showing incsufficient develop or exposure</p></figcaption></figure>

***

### Additional Resources

See this webpage for in depth spin coating theory: [https://www.ossila.com/en-us/pages/spin-coating](https://www.ossila.com/en-us/pages/spin-coating)

[AZ-P4210 techsheet](https://www.microchemicals.com/micro/tds_az_p4000_series.pdf)

[AZ 400K developer](https://www.microchemicals.com/micro/info_az_400k_421k_Developer.pdf)

### Alternative Exposure Technique: 365nm Flashlight

1. Put on UV protection glasses.
2. Before placing the chip under the exposure area, turn on the flashlight and adjust the position of the UV meter’s sensor head to maximize the reading.
   1. Depending on the battery level, this should be around 10 mW/cm2.
3. Turn off the flashlight, being careful not to move it out of position.
4. Place the chip on the plastic cap photoresist side up.
5. Place the mask on the wafer. Gently press down to sandwich the two together.
   1. If the ThorLabs logo is correctly oriented then the chrome is facing you. Put that side face down towards the chip.
   2. Try not to slide the mask on the wafer because you’ll damage the photoresist.
6. Place the cap with the wafer and mask on top of the UV sensor.
7. Turn on the flashlight for the desired exposure time.
8. Record the measured exposure time in the [spreadsheet](https://docs.google.com/spreadsheets/d/1T9-kXXxdD9c6KZh_iy1LGt8I8wGlmeVlIZmvBrkVQ2g/edit?usp=sharing)
   1. Dose should be automatically calculated in the sheet based on exposure option used

## Troubleshooting

If horizontal bands appear in Flir-based camera preview:

1. Open the Flir camera viewer.
2. Select the connected Flir camera model (Blackfly S) and select the green triangle. You should see a preview of the camera's output (it may appear black or grainy; this is okay).
3. Update the camera settings so that Acquisition Frame Rate Enable, Acquisition Frame Rate, Exposure Auto, and Exposure Time have the same values shown below:

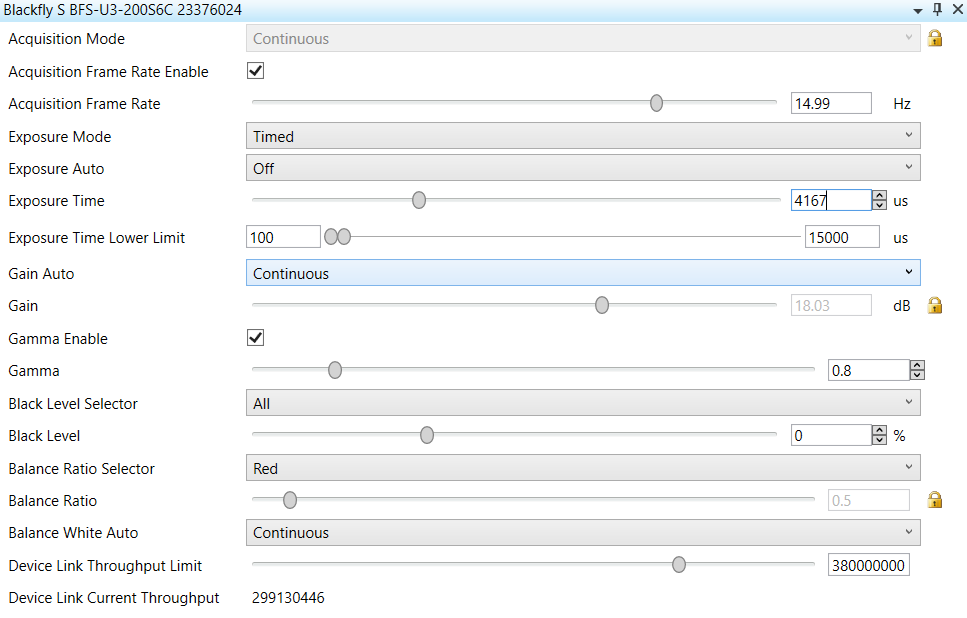
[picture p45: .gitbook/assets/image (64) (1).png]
<figure><figcaption><p>Example Flir Blackfly S Camera Settings</p></figcaption></figure>

4. Verify that the horizontal bands are no longer present across the camera preview. This may be easier when viewing the stage or a chip while illuminated with the projector.

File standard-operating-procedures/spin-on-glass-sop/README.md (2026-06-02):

---
layout:
  width: default
  title:
    visible: true
  description:
    visible: true
  tableOfContents:
    visible: true
  outline:
    visible: true
  pagination:
    visible: false
  metadata:
    visible: true
  tags:
    visible: true
  actions:
    visible: true
---

# Spin on Glass/Diffusant SOP

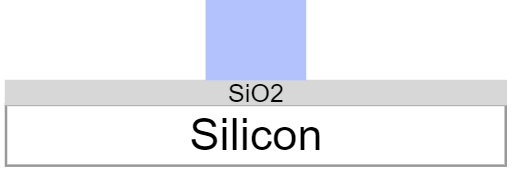
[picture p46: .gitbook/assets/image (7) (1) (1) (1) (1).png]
<figure><figcaption><p>Before Spin on Glass (SOG)</p></figcaption></figure>

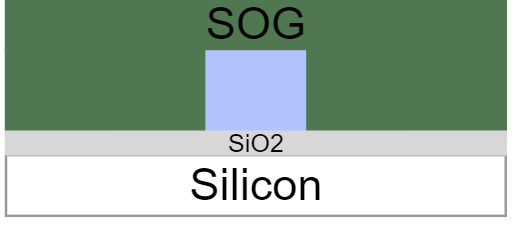
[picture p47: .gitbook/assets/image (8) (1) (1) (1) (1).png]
<figure><figcaption><p>After Spin on Glass (SOG)</p></figcaption></figure>

## Process Parameters

***

| Total Time                                                                 | 15-35 minutes                                                            |
| -------------------------------------------------------------------------- | ------------------------------------------------------------------------ |
| Spin Speed                                                                 | 4000 rpm                                                                 |
| Spin Time                                                                  | 20s                                                                      |
| Anneal Temperature Profile \[temp 1, time 1, temp 2, time 2...] \[°C, min] | **700B**: \[400, 20-30], **P504**: \[200, 10-15], **B154** \[200, 10-15] |

***

## Purpose

Three types of "spin on glass" are currently used in the Hacker Fab. 700B, P504, and B154, all three sourced from Filmtronics. Each of these begin as liquids, which are spun onto the surface of the chip, then annealed to form solid thin films. This is known as a sol-gel process.&#x20;

700B becomes an undoped thin film of SiO2, but with lower density than a thermally grown SiO2. After high temperature exposure (\~1100C) this thin film densifies to the density of a thermally grown oxide.

P504 becomes a thin film of SiO2, with a small amount of Phosphorous in it, also with lower density than a thermally grown SiO2. This is also referred to as a "spin on diffusant." After high temperature diffusion (\~1100C) this thin film densifies to the density of a thermally grown oxide.

B154 does not have SiO2 precursors like 700B and P504, but becomes a solid thin film with a small amount of Boron in it. The composition of this solid film after relatively low temperature exposure (\~200) is not clear, since the formula is proprietary, but it is believed to be some sort of polymer. Upon diffusion (exposure around \~1100C) the B154 thin film becomes SiO2 of thermally grown density.

These spin on glass films are often etched with a dilute HF solution, or BOE (HF + NH4F) due to the high selectivity with Si. However, the etch rate of spin on glass annealed around 400C is much faster than that of spin on glass that has been densified at around 1100C. Additionally, the B154 film that has been annealed at 200C is not effectively etched with HF, but is effectively etched with HF after diffusion at 1100C.

As indicated above, the purpose of the P504 and B154 deposition is to create a dopant source at the surface of the silicon, which can be diffused into the silicon substrate. 700B is used as a diffusion barrier, or a dielectric layer to fabricate metal interconnects on top of.

### Defects

The main concern with spin on glass, is its tendency to crack (extent of cracking varies, but full shatter can occur leading to flake off), have variation in uniformity, and have pinholes. Cracks and pinholes can lead to uneven doping across the surface, failure of 700B to act as a diffusion barrier, or metal interconnects shorting to the Si below. Factors like humidity, annealing temperature profile, particulate contamination, and shelf life of the spin on glass solution.

However, the CMU Hacker Fab has found particulate contamination to be the number one cause of defects, and this issue has been mitigated greatly by using filtered syringe tips during deposition, as seen below in the procedure.

***

## Tools

3. [Vacuum Spin Coater](../patterning-sop-stepper-v2/vacuum-spin-coater-sop.md)
4. [Hot Plate](../patterning-sop-stepper-v2/hot-plate-sop.md)

## Materials

1. Filmtronics 700B, P504, or B154.
   1. [Storage and Preparation](spin-on-glass-storage-and-preperation.md)
2. Acetone
3. Isopropanol

***

## Procedure

### Wafer Cleaning

1. Check that the working volume of spin on glass is labeled with the date it was poured. For 700B and P504, ensure that the solution has not been out for more than a month (main bottle is stored at 5C).
   1. If you are pouring a new working volume of P504 or 700B, let it come to room temperature before using it (ideally, wait 24 hours).
2. Preheat the[ Hot Plate](../patterning-sop-stepper-v2/hot-plate-sop.md) to 100°C
3. In the fume hood, hold the wafer with tweezers over the sink.
4. Rinse the polished side of the wafer thoroughly with acetone, then isopropyl alcohol.
   1. The acetone leaves a residue that must be removed by the isopropyl alcohol rinse.
5. Blow the wafer dry with the nitrogen gun by pressing the wafer against a cleanroom wipe on the table to ensure it does not fly away. **Get a good grip on it with your tweezers**.
   1. Even when the wafer appears dry, there may still be moisture on the edges, so dry both sides liberally for \~20 seconds
   2. if there is visible acetone residue after drying, repeat steps 2-3

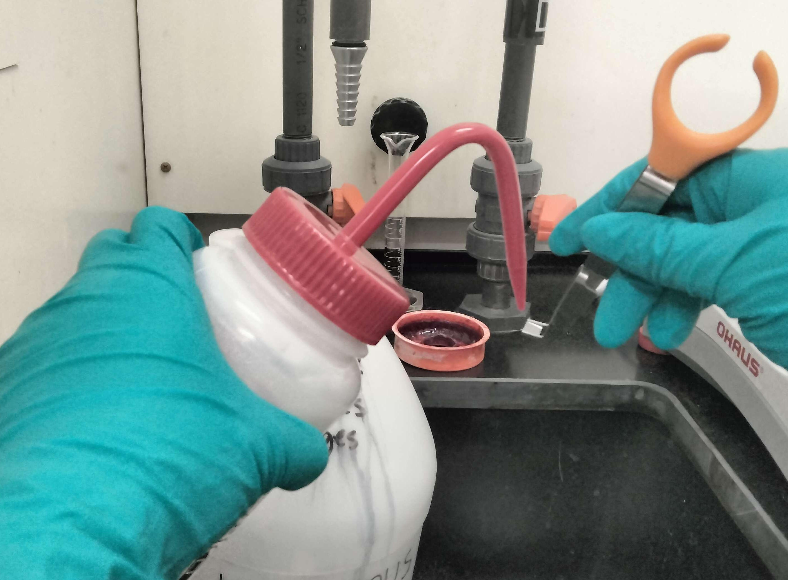
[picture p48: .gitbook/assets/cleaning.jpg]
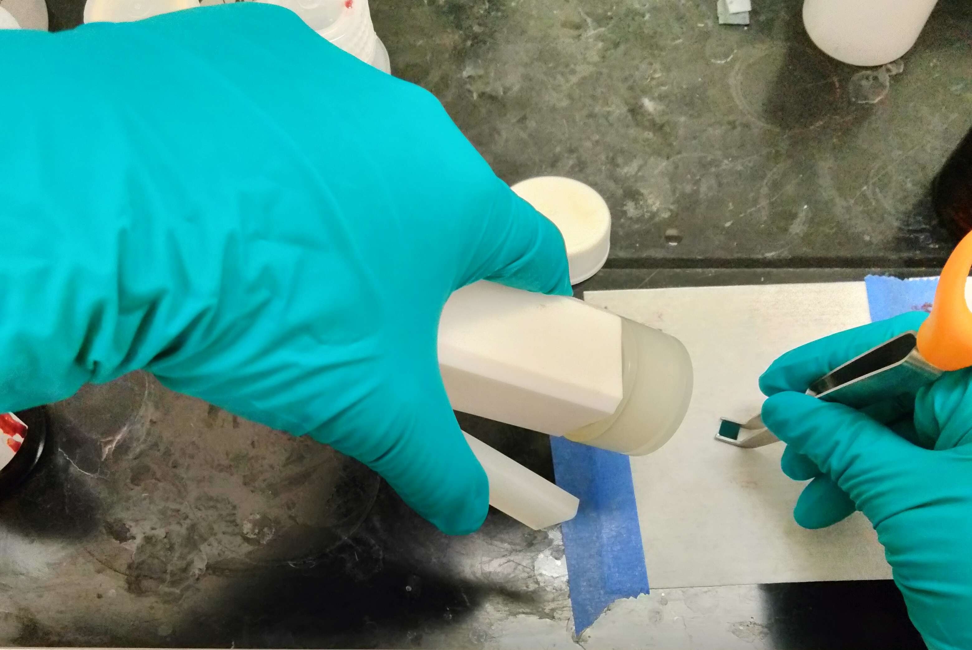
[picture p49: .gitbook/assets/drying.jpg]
<div><figure><figcaption><p>Acetone rinse</p></figcaption></figure> <figure><figcaption><p>Drying with nitrogen gun</p></figcaption></figure></div>

### Prebake

4. Place the wafer in the **center** of the hotplate for 20 seconds
   1. Be sure to handle the wafer with tweezers that can handle high temperatures (metal tweezers)
   2. No need to turn the hotplate off since annealing will require 100°C initially as well

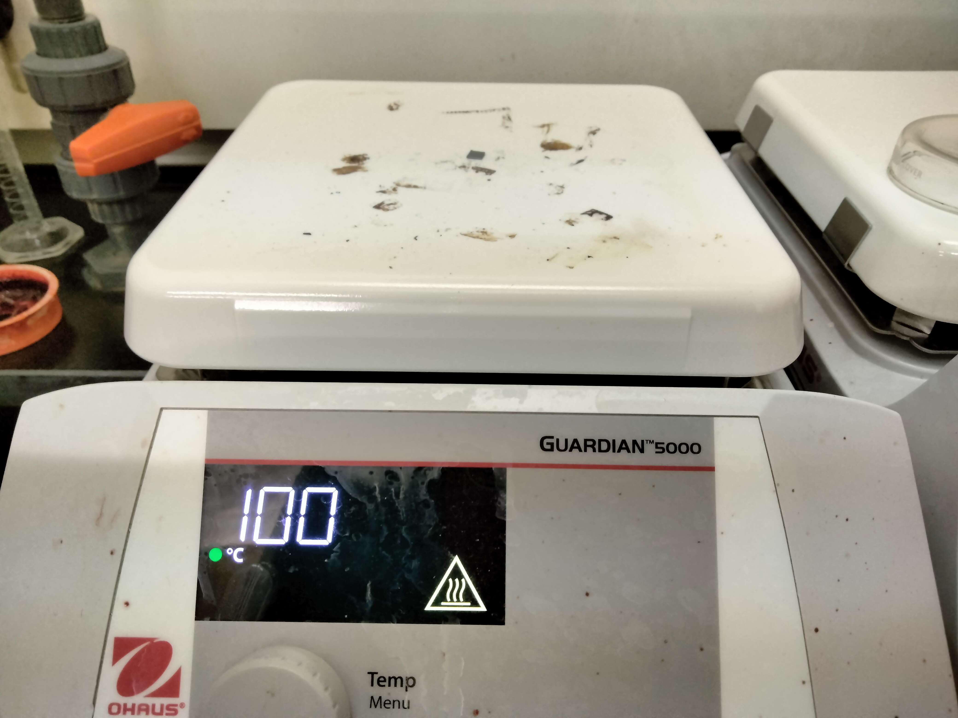
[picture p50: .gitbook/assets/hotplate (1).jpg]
<figure><figcaption><p>100C hotplate with chip in the center</p></figcaption></figure>

### Spin Coat

6. Place wafer onto the chuck of the [vacuum spin coater](../patterning-sop-stepper-v2/vacuum-spin-coater-sop.md)
7. Open the SOG container while keeping the bottom resting on the table
   1. Never open containers up in the air or outside of the fume hood
8. Pipette **1-2 drop** of SOG using Luer Lock filtered syringe:
   1. Take a clean syringe and draw it up \~½ to create an air pocket in the tube
   2. Suck up SOG about halfway up the syringe. This is a lot more than you need for 1 drop, because the filter needs to be wetted by the excess solution before drops are released.
   3. Twist on a syringe filter
   4. Release 2 drops back into the SOG container
   5. Apply 1 or 2 drops to your chip, make sure the chip is completely coated in solution but do not use more than 2 drops
   6. Dump any remaining SOG in the syringe back into the SOG container
   7. Dispose of the syringe and the filter in the waste bucket

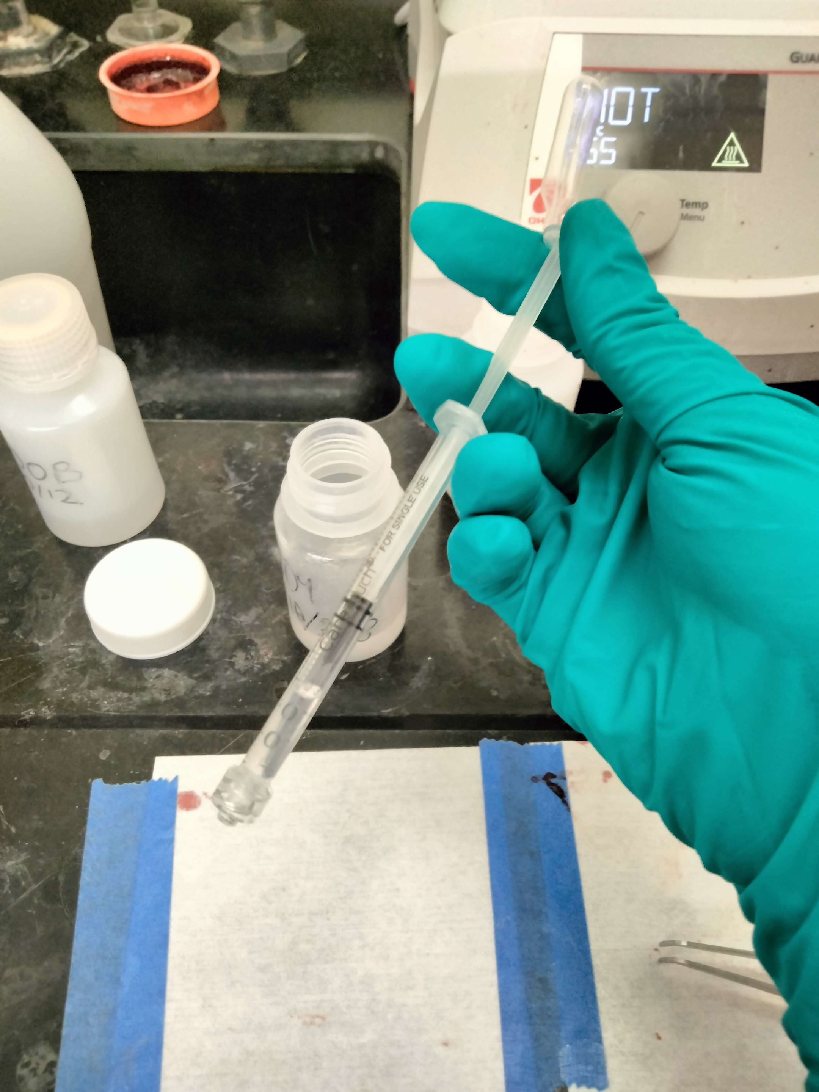
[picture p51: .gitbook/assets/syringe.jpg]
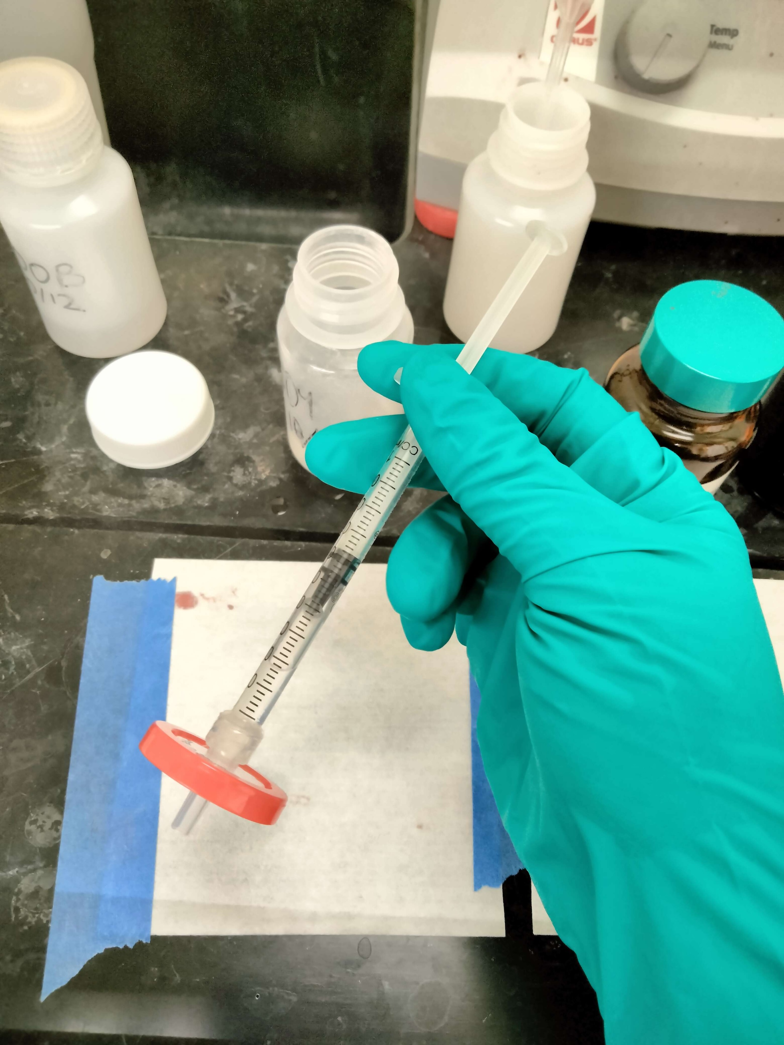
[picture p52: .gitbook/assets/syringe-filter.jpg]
<div><figure><figcaption><p>Pipette with SOG and air pocket</p></figcaption></figure> <figure><figcaption><p>Pipette with filter</p></figcaption></figure></div>

6. Spin coat the wafer <mark style="background-color:orange;">(Remember to switch on the vacuum!)</mark>
   1. After spin coating, the SOG application should appear even. (See pictures below)
7. Immediately move onto annealing

### 

### Hot Plate Annealing.

12. The hot plate should already be at 100C
13. Place wafer onto the center of the [Hot Plate](../patterning-sop-stepper-v2/hot-plate-sop.md)
    1. Be sure to handle the wafer with tweezers that can handle high temperatures
14. Set the hotplate to the desired annealing temperature (200C for P504 or B154, 400C for 700B)
15. After the desired anneal time has passed (10-15 minutes for P504 and B154, 20-30 minutes for 700B), use metal tweezers to remove the chip. Be careful not to burn yourself.

### Tube Furnace Anneal/Diffusion P504

If the next step requires higher temperatures, see the [Tube Furnace SOP](../tube-furnace-sop.md) for details.

### Inspection

See [Inspecting SOG wafers](spin-on-glass-inspection.md) document for a more detailed overview of failure conditions and possible causes.

## Safety

Be sure to work under fume hood when working with SOG. The SOG can give off toxic vapors (especially during annealing)

DO NOT touch the hot plate during operation. A 400 C hot plate will cause severe burns. (Reminder: 400 C = 752 F). The same is true of the glass cover, which is why it is important to ramp down before touching.

<br>

***

<br>

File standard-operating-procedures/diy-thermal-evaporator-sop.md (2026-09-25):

---
cover: ../.gitbook/assets/IMG_5114.jpg
coverY: 0
---

# Thermal Evaporator SOP (CMU Version)

### Materials

<div><figure><figcaption><p>Laptop with STM2 software and STM2 monitor plugged in</p></figcaption></figure> <figure><figcaption><p>Double sided polyimide tape, tungsten filament, and high purity Al wire (99.999%)</p></figcaption></figure></div>

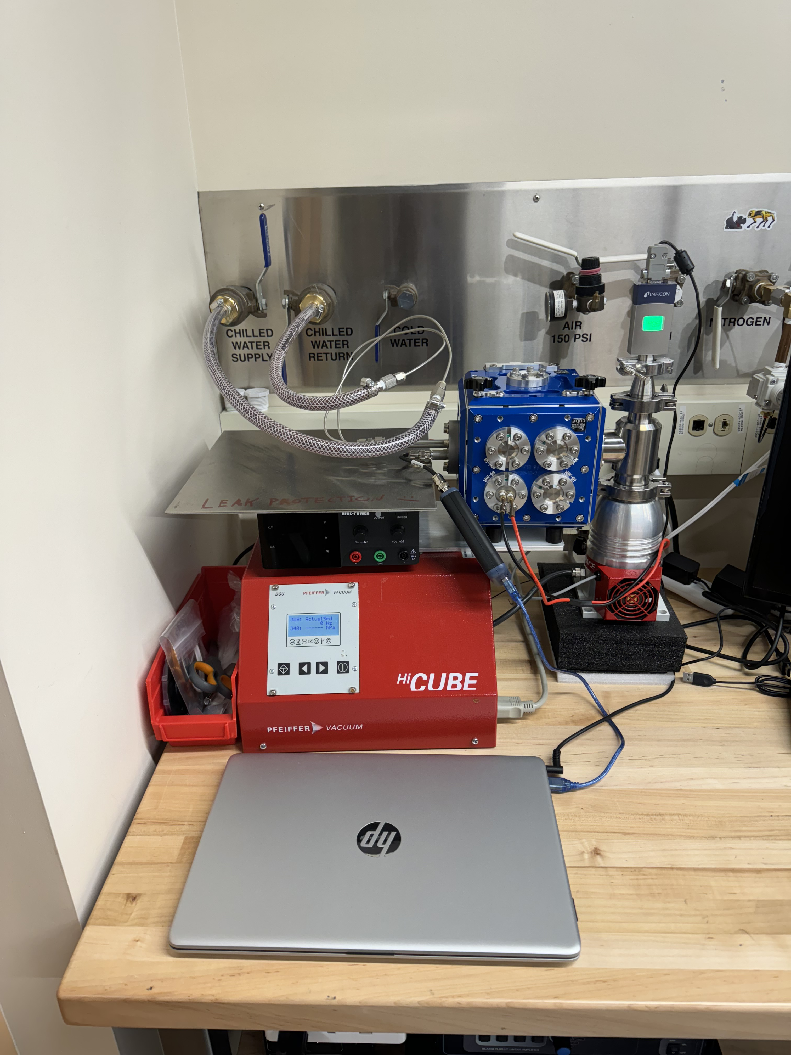
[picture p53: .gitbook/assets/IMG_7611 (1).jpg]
<figure><figcaption><p>Chamber</p></figcaption></figure>

### Procedure

* Put on nitrile gloves to prevent contaminating the chamber.
* If the Pfeiffer turbo pump is on, power it off by pressing the rightmost button beneath the green LED:

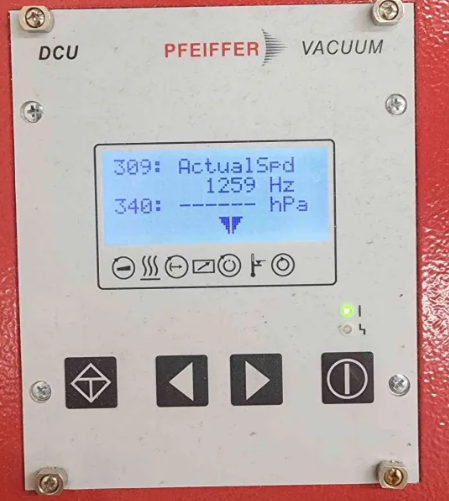
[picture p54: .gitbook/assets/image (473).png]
<figure><figcaption></figcaption></figure>

* Use the arrows to scroll to parameter 309, which show pump speed.
* Wait until the pump speed is at 0Hz.
* Slowly vent the chamber by unscrewing the vent screw located on the turbo pump.

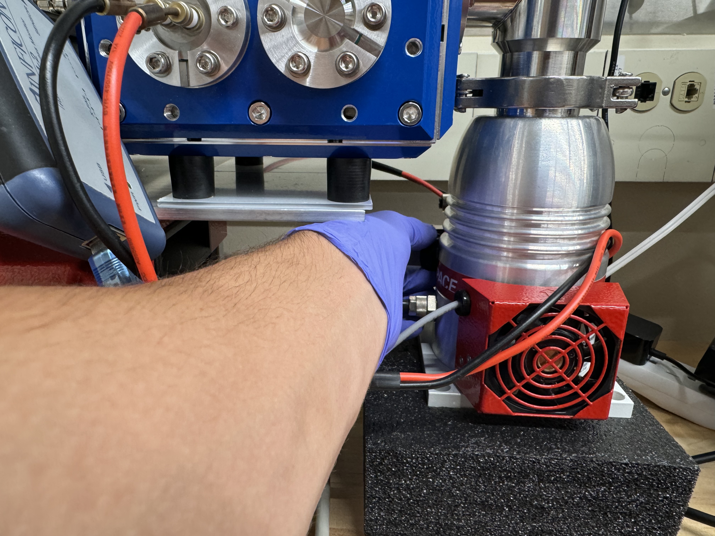
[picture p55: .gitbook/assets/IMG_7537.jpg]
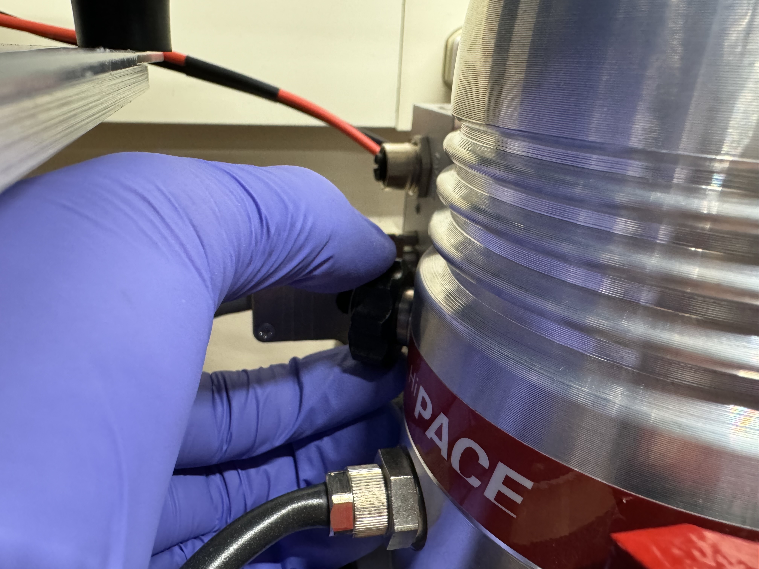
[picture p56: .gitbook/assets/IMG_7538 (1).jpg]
&#x20;

* Wait until the pressure is at 1E3 hPa or greater (pressure is given by parameter 340 - scroll to it with the arrows).
* Unscrew the two black knobs pictured below, then lift the chamber lid.

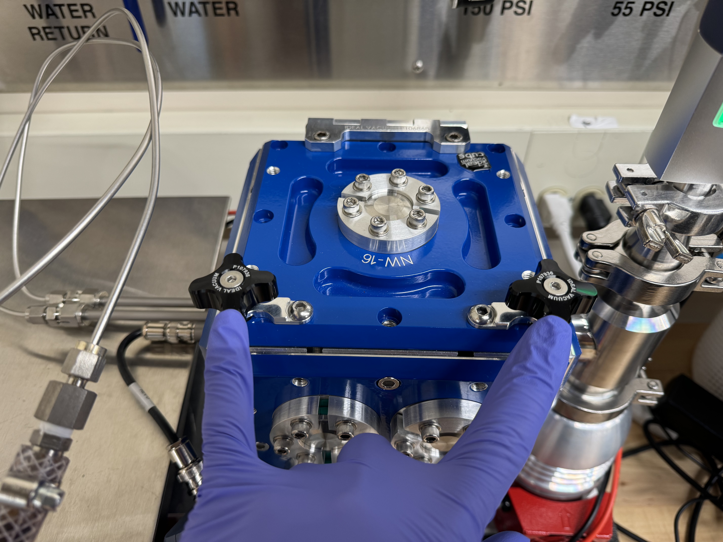
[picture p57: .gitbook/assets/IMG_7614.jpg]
<figure><figcaption></figcaption></figure>

* Turn the two black knobs on the top of the blue box as shown above and open the lid.
* The tungsten filament is secured with two barrel connectors pictured below. The filament can be removed by slightly loosening the screws closest to the filament.

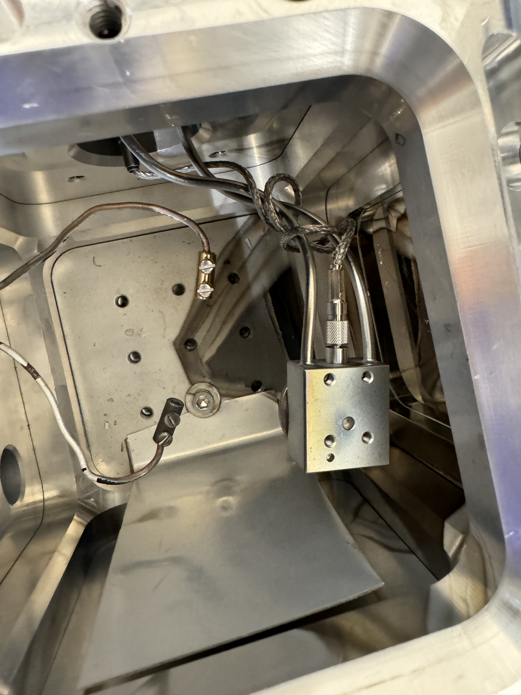
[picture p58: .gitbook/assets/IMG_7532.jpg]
&#x20;

*   Tightly wrap aluminum wire near the center the W coil, you only really need an inch of wire. Due to the alloying between Al and W, the filament becomes more brittle after each evaporation, so be careful not to break it. If you do break it, use a new filament. You may have to use clippers to shorten the ends of the new filament to get it to fit right. &#x20;

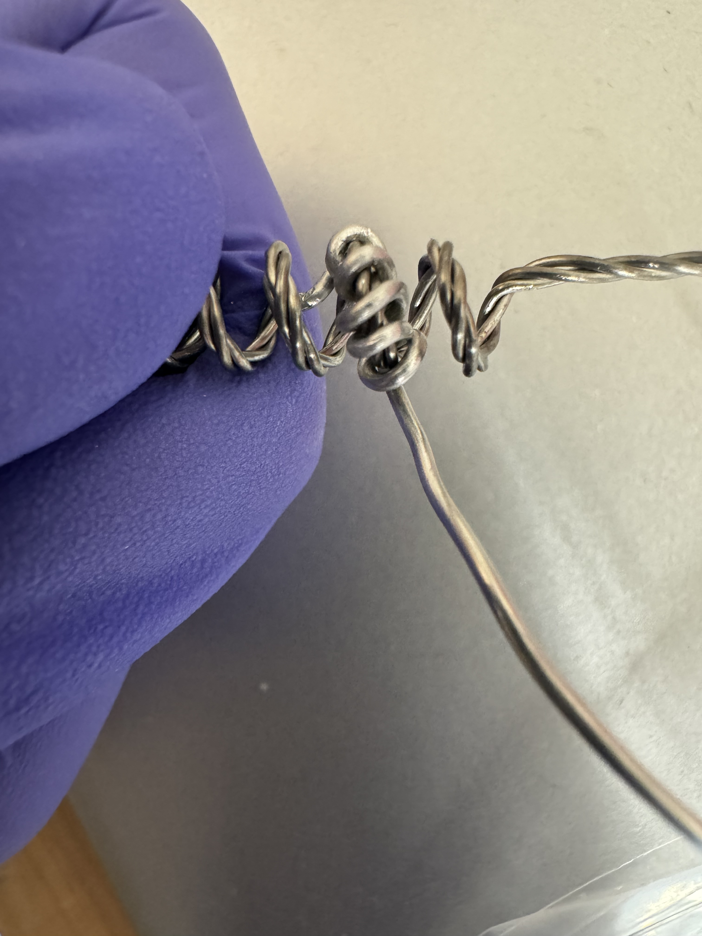
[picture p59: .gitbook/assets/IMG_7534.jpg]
    <figure><figcaption></figcaption></figure>
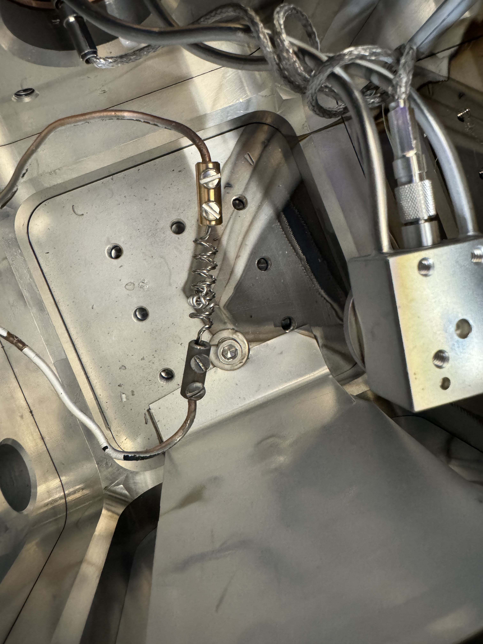
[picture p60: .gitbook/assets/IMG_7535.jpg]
* Place the tungsten filament back and screw it in. Make sure it is straight. 
* Place \~ 1 inch of polyimide tape on the substrate holder shown below, then peel off the clear layer on top of the tape. Since aluminum covers the entire interior of the chamber, when you put the tape on, aluminum might stick to it and flake off. Just continue attempting to apply tape until it stick without flaking off. Note that it must be polyimide/Kapton tape, otherwise it will outgas under vacuum.

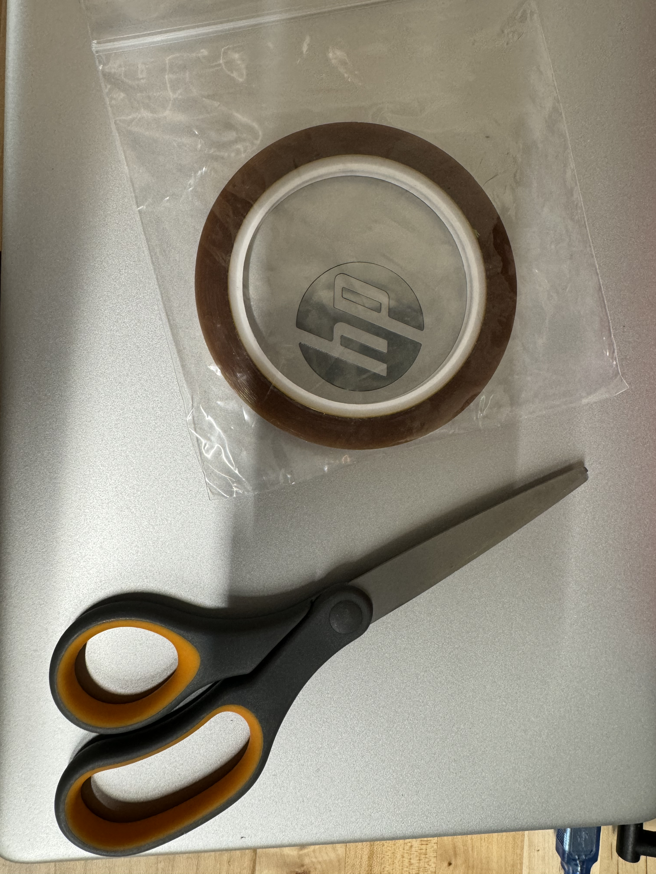
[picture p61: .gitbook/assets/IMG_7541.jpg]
<figure><figcaption></figcaption></figure>

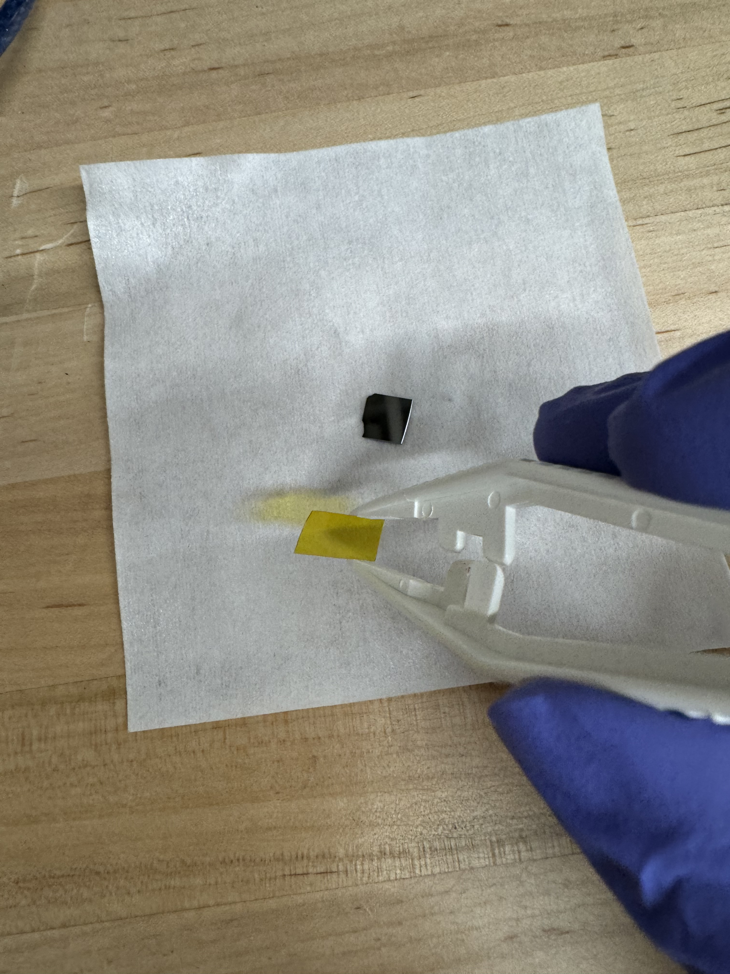
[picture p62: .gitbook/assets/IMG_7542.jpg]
<figure><figcaption></figcaption></figure>

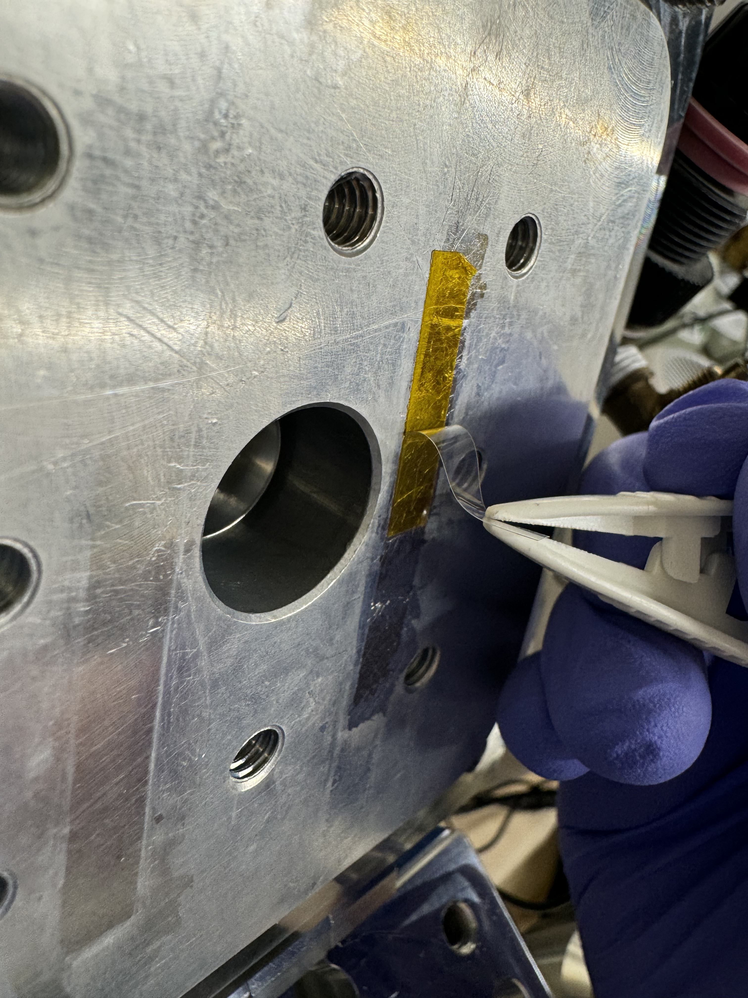
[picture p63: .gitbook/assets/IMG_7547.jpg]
<figure><figcaption></figcaption></figure>

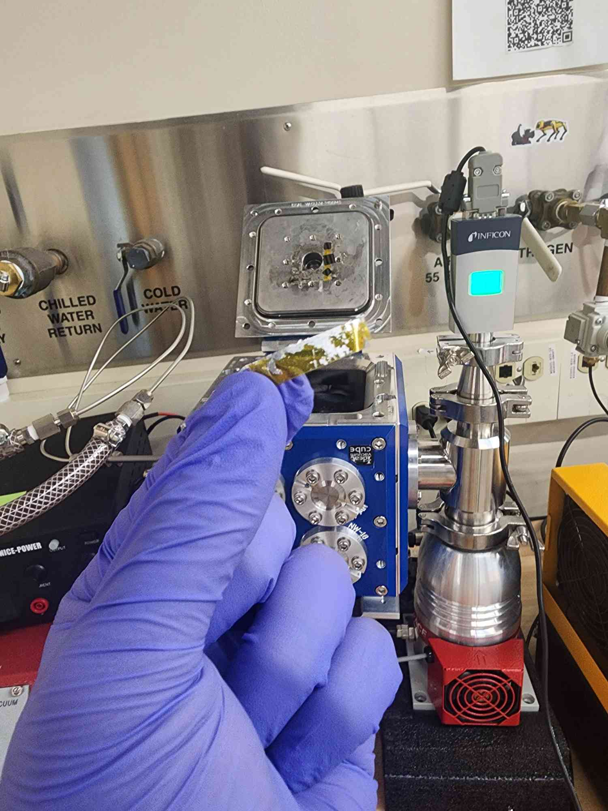
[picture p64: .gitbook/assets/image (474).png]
<figure><figcaption></figcaption></figure>

<figure><figcaption></figcaption></figure>

* Place your chip on the tape, and use tweezers to gently press down on the corners of the chip.
* Double check that the wire and barrel connectors are suspended and not touching anything conductive (including the chamber).
* Close the blue lid and screw the black knobs all the way.
* Close the vent all the way (hand tight).
* Turn on the pump. Monitor the pump speed in Hz. Often, around 270Hz, it makes a bad noise and stops speeding up. This can be resolved by quickly turning the pump on and off with the button on the right. It will slow to \~160Hz, then re-speed up, and pass the point at which it got stuck. This is not normal pump behavior, and we are looking into a repair.
* Screw the black knobs more since they tend to loosen after the pump turns on.
* Wait for the pressure to reach 3.71E-5 torr (lower limit of the Pirani gauge). This may take hours. However, with this system, very conductive films have been deposited at a pressure of only 1E-4 torr when there was a bad seal. If you choose to do this, you are sacrificing some film quality.
* Turn on the water cooling for the QCM sensor head. Off is when both handles are vertical, on is when both handles are horizontal.

<div><figure><figcaption><p>On</p></figcaption></figure> <figure><figcaption><p>Off</p></figcaption></figure></div>

* Turn on the HP laptop and open the STM-2 software. Under the STM-2 tab, it should show a connection to a sensor. Then, the frequency value should read something near 6 MHz, and actively stream slight noise oscillations.

<figure><figcaption></figcaption></figure>

* Hit the start button - values should pop up for both rate and thickness. Rate should be streaming noise oscillations near 0.
* For the next step, do not touch the wires going into the chamber. If anything starts smoking, or if current is flowing but the deposition rate does not increase, you must turn off the power supply immediately.
* Turn on the power supply. Set it to 45 amps or less with the current knob; when ready, begin flowing the current by pressing the white "output" button. Deposition rate will soon shoot up to hundreds of Angstroms per second, then you've reached the desired thickness in kilo-Angstroms, hit the white output button to turn off the current.

<div><figure><figcaption><p>On</p></figcaption></figure> <figure><figcaption><p>Off</p></figcaption></figure></div>

* Power off the power supply.
* Turn the pump and water cooling off.
* Wait until parameter 309 shows 0Hz, indicating the pump has fully stopped.
* Slowly unscrew the vent until chamber is at \~760 torr.
* Open the lid.
* Peel the piece of tape with your chip off.
* Grip the sides of the chip with the reverse plastic tip tweezer shown below, then peel the tape off with another tweezer.

<div><figure><figcaption></figcaption></figure> <figure><figcaption></figcaption></figure></div>

### Troubleshooting

* If current is not flowing when you press output on the power supply, then the electrodes are probably not connected through the filament. Check this by disconnecting the power lines from the back of the power supply, then use a multimeter on each electrode to see if it is an open circuit. If so, then a connection to the filament is not on.
* No deposition: check that nothing is shorted, preventing full current flow through the filament.
* Kapton tape not sticking - make sure to peel off any aluminum deposited onto the chamber wall so you can properly adhere the tape.

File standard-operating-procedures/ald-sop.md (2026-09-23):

---
description: >-
  Contacts: Matt Moneck (mmoneck@andrew.cmu.edu), Jay Kunselman
  (jskunsel@andrew.cmu.edu), Joel Gonzalez (bgonzale@andrew.cmu.edu)
---

# ALD SOP

## System Description and Diagrams

Before operating this system, you should familiarize yourself with ALD and the documentation for the build of this system. This will let you get a working understanding of the system so that you understand the operating procedure.&#x20;





<br>







**Legend**

1. Exhaust line for scroll pump
2. Vent line for precursor box.
3. System control monitor with GUI displayed
4. Carrier gas + precursor delivery line
5. Precursor box
6. Vacuum Chamber
7. Vacuum Pressure Gauge
8. Control electronics housing
9. Computer
10. Emergency power off button and housing
11. Variac (for delivery line and ampule heating)
12. Storage container (replacement filter traps)
13. DC Power supply (for substrate heater)
14. Scroll Pump
15. Carrier Gas Cylinder (UHP Nitrogen)
16. Mass Flow Controller (MFC)
17. Dual stage pressure gauge for carrier gas
18. Pneumatic gas valve 1 (large)
19. Pneumatic gas valve 1 (small)
20. Pneumatic gas pressure regulator
21. Delivery line Thermocouple
22. ALD valve 1/3 (actuated with pneumatic gas)
23. Manual valve for precursor ampoule
24. Precursor ampule (DI water shown)
25. Flow sensor (for monitoring precursor box venting)
26. Substrate heater/stage
27. High current heating wire
28. J-type thermocouple
29. Ammonia sorbent filter trap (POSI-trap from Mass Vac Inc)
30. Activated charcoal filter trap (POSI-trap from Mass Vac Inc)
31. Stainless steel gauze filter trap (POSI-trap from Mass Vac Inc)
32. Blast gate for precursor vent line
33. Blast gate for scroll pump exhaust line

## System Performance Summary (Based on Validation Testing)&#x20;

The ALD system has been experimentally validated to operate within a pressure range of 250–1000 mTorr, with stable control achieved via N₂ mass flow controller modulation.&#x20;

Substrate heater stability of ±5°C has been demonstrated across 100–250°C.&#x20;

The system supports pulse-based operation with measurable pressure response for pulse durations as low as 50 ms, confirming suitability for ALD processes.

## Pre-Operational Safety Checks

* PPE: Put on nitrile gloves and safety glasses
* Fire extinguisher: Identify the nearest unit (mounted on the right-side wall next to the workstation table) and perform a visual check to ensure:
  * The pin and safety seal are intact
  * The inspection tag is current
  * The extinguisher is unobstructed and nothing is stored in front of it



* Fire alarm: Familiarize yourself with the location of the closest building fire alarm pull station. The nearest fire alarm pull station to the REH204 is at the nearest exit. To get there, turn left when exiting REH204, go to the end of the hall, you will find the pull station next to the exit door.



*   Precursor Box Inspection

    *   Heating tape and thermocouple adhesion: All heating tapes are properly wrapped around precursor ampoules and delivery lines, with thermocouples securely adhered beneath the tapes.

        * Visual inspection:
          * Ensure all heating tapes (up to 3 inside of the precursor box, 1 for heating line, two for precursors) are securely wrapped onto the precursor ampule or delivery line. There should be no loose heating tapes.
          * Ensure that each heating tape has an associated thermocouple securely taped to the corresponding ampule or delivery line.&#x20;
          * Inspect heating tape for fraying, tears, loose wrapping, or exposed wiring.
          * Check for discoloration or darkened areas, which may indicate overheating.
        * Example of properly mounted heating tape and thermocouple

        
    * Ensure all manual ampule valves are closed (knob should be horizontal as shown)

    

    * Ensure thermocouples are electrically isolated from any metal surfaces (e.g., wafer plate). Direct contact can introduce electrical noise and lead to unstable or incorrect temperature readings.
    * Verify that all thermocouple attachments are secure and not loosely placed under heating tape.
    * Check for proper insulation of delivery lines and precursor heating zones to minimize heat loss and prevent control instability.
*   Venting and Gas Flow checks

    * Open the computer (password is written beneath the monitor). Open the app named “ALD GUI”. Press the "Connect" button to have the computer connect to the microcontroller and begin streaming data from the thermocouples.
      * Verify that all electrical connections, especially at the DC power supply terminals, are secure. Loose connections can result in fluctuating or incorrect temperature readings.
      * Ensure thermocouple wiring is intact and not in direct electrical contact with conductive components.
      * Inspect for any abnormal sensor readings before operation; unstable readings may indicate electrical interference or poor connections.&#x20;
    * The flow rate displayed on the mass flow controller for the carrier gas should be set to 0 SCCM.
    * Ensure the precursor box flow velocity is greater than 2 m/s (displayed on the GUI) , and that there are no alarms present on the GUI.&#x20;
    * Ensure the “blast gate” is in the open position for both the precursor box vent line and the pump exhaust line (as shown)

    

    * Confirm that pressure readings are stable at baseline before initiating any pulse or flow adjustments. Excessive noise in pressure readings may indicate sensor or signal processing issues.
    * If pressure signal fluctuations exceed expected pulse magnitudes (\~2–3 mTorr), consider verifying signal averaging or filtering settings in the control system (GUI)
* Vacuum Chamber and Scroll Pump Inspection
  * Open the chamber door. Ensure there is no obvious particulate on the o-ring that could prevent a good seal. Ensure the o ring is sitting within the groove along the door perimeter
  * Ensure the copper heating wires for the substrate heater are not making contact with any part of the chamber or bracket.
  * Ensure the substrate heater thermocouple is secure into the substrate heater.
  * Ensure that the scroll pump power cord is directly connected to a permanent electrical wall outlet and not a power strip.
  * Ensure that the scroll pump vent line (1)  is attached at the pump outlet and the blast gate (33).

If any of the above items are not satisfied, DO NOT operate the ALD chamber or any associated equipment until resolved. Please report them to the lab manager to be resolved.

## Loading the Substrate and Pumping Down

1. Use the “CMU Hacker Fab Lab/Tool Usage” shared Google Calendar to block out the time you will be using the ALD System. Label your calendar event “ALD\_name.” This should include the 24 hour pump down time, recipe execution, and removing the substrate (more detail below).
2. Put on nitrile gloves and safety glasses.
3. Open the vacuum chamber door, and place the substrate centered on the substrate heater.
4. Close the chamber door, then simultaneously/evenly tighten the door screw knobs until hand snug.
5. Turn on the scroll pump with the green button on the back of the pump.
6. Once the pressure is below 1 torr, re-tighten the door screw knobs (low pressure pulls door closed tighter)
7. Wait until the vacuum pressure gauge reads 50 millitorr or less. This will take \~24 hours.

**From now until the end of the substrate is removed, the system must be attended to at all times.** Lab members are expected to coordinate with each other to ensure that at least one person is in the lab throughout the process. It is recommended that at least two lab members are present so that one can leave to go to the restroom, take a break, etc. There is a zero-tolerance policy for leaving the ALD chamber unattended during deposition. This is due to the pyrophoricity of the precursors being used and the need for immediate intervention in the event of an emergency.&#x20;

## Turning on Carrier Gas Flow

1. Open the valve on the UHP Nitrogen Cylinder (lefty-loosey aka CCW)



3. Ensure the gauge on the right side is >500 PSIG, and the left gauge is between 10 and 30 PSIG as seen below. If not, contact the lab manager.



4.  Locate the Mass Flow Controller and follow the instructions below to begin flowing carrier gas.

    * Initial state - mass flow is 0 SCCM. Press on “set pt”:

    

    * Press on “select digit” to select which digit you're changing:

    

    * Once you have navigated to the correct digit you want to change, you can press the “up” and “down” buttons until you reach the desired setpoint. The desired setpoint is process dependent! Ensure you have planned out what flow setpoint you intended to use. This setpoint should be informed by literature review related to your process, as well as testing of pressure/flow relationship:

    

    * Press “set” to set the flow:

    
5. The MFC should now reflect the setpoint you entered, and the chamber pressure should increase. After a few minutes, the chamber pressure should be stable at your desired pressure. Again, the desired pressure is process dependent.

## Turning on Pneumatic Gas

Refer to the following instructions for how to turn on the pneumatic gas.

* Pull the large white lever (pneumatic gas valve 1) to the open position:

<figure><figcaption></figcaption></figure>

* Turn the small black knob (pneumatic gas valve 2) to the open position:

<figure><figcaption></figcaption></figure>

* Ensure the pressure regulator reads \~75 PSIG:



## Turning on Heating Elements

1. Turn on the variac, and ensure it is set to 50V as seen below.



2. Turn on the DC power supply. When it turns on, current should read 0 amps and voltage should read 15 volts. Later, when you set the substrate temp setpoint, the current will rise to 10 amps, or whatever current you're choosing to use.



3. Open the ALD GUI.
4. On the Control tab, entire the desired temperature setpoints for the precursor(s), delivery line, and Substrate heater. All of these setpoints are process dependent and should be informed by literature review.
5. The DC power supply should show 10 amps while the substrate heater heats up, as seen below.



6. Wait for all temperature setpoints to stabilize. There will be temperature overshoot at first due to the nature of the control system.
7. If temperature overshoots any setpoint by >50C, hit the emergency power off button and contact the lab manager.
8. If temperature does not rise or stabilize on any given element, contact the lab manager.
9. You may not leave the system unattended while waiting for temperature to stabilize!

## Deposition

1. Open the precursor box. Open the manual valve associated with each precursor ampule. Each knob should be parallel to the ampule as seen below. When opening the door, a loss of vent flow alarm should come on, and then turn off after closing the door.



2. Open the recipes tab. Build or open a desired recipe (process dependent).
3. Run the recipe. You should hear the ALD valves begin to actuate.
4. You may not leave the system unattended while the recipe is running! The deposition process must be attended at all times. Lab members are expected to coordinate with each other to ensure that at least one person is in the lab throughout the process. It is recommended that at least two lab members are present so that one can leave to go to the restroom, take a break, etc. There is a zero-tolerance policy for leaving the ALD chamber unattended during deposition. This is due to the pyrophoricity of the precursors being used and the need for immediate intervention in the event of an emergency.&#x20;

This image shows the precursor cylinder used during deposition tests, wrapped with insulation and heating tape to ensure stable temperature control and consistent precursor delivery.



## Removing Substrate

1. After the recipe is complete, reset all temperature setpoints to 20C, and wait for them to cool to 30C or lower.
2. Turn off the Variac and DC power supply.
3. Open the precursor box and close all the manual ampule valves as shown.
4. Set the Mass flow controller back to 0 SCCM.
5. Close the UHP Nitrogen carrier gas cylinder valve (righty-tighty)
6. Close both the small back and large white pneumatic gas valves.
7. Close the GUI.
8. Turn off the Scroll pump with the red button on the back.
9. Once pressure has returned to 760 torr or above, open the chamber and retrieve your substrate.
10. Reclose chamber door.



### Precursor Gas Procedures (storage, handling, replacement)

* Precursors acceptable for use in this system:
  * Non-pyrophoric and non-chlorine based precursors
    * Pyrophoric precursors may be approved in the future, but must be pre approved by the ECE Nanofab and EHS.
* There is no location for precursor storage within the CMU Hacker Fab. There may only be precursors in the precursor box, which are hermetically connected to the ALD systems delivery line via a VCR fitting (prepared for use with the ALD system).
* Precursors are to be sourced from the CMU Bertucci Nanofab through Matt Moneck.
  * Handling / Replacement of Precursor Ampoules is only to be performed by Matt Moneck.

## Troubleshooting Guide

* The substrate heater won't heat up.
  * If the DC power supply does not show 10 amps after setting temperature, either...
    * The relay is not actuating, or
    * One of the leads is disconnected, making an open circuit
  * Otherwise...
    * Heating wire may be shorted to the chamber or thermocouple dislodged. Power off DC power supply. Open the chamber and check for any unintended contact between the heating wire and chamber. Check if the thermocouple is secured within the heater assembly.
* The chamber won't pump down.
  * Possible causes...
    * Leak: check seal cleanliness and retighten with even pressure on each screw knob.
    * Carrier gas not off: ensure MFC is set to 0 SCCM.
    * Vacuum gauge broken: if the door wont open, but the pressure is at atmosphere, then the gauge may be broken and should be reported to the lab manager.
    * Manual ampoule valve open: ensure all manual ampoule valves are closed.

### Emergency Response Procedures

There are two ways to stop the deposition process during an emergency. One way is through the GUI’s “emergency stop” button. This will shut off all electricity to the components, and in order to restart, you will have to close and re-open the GUI.&#x20;



Another option is the physical emergency stop button (labeled “10” in system diagram). This button achieves the same goal as the GUI’s emergency button, but it is a physical button located next to the deposition chamber.&#x20;



Below is a list of possible scenarios...

* Fire:
  * If safe to do so, press the Emergency Stop (E-STOP) button.
  * Activate the building fire alarm system using the manual fire alarm pull station in the hallway (at nearest exit, identified in pre-operational checklist).
  * If you have been trained to use a fire extinguisher and the fire is small, attempt to extinguish the fire (only if you are comfortable doing so). Use the nearest appropriate fire extinguisher.
  * Evacuate the building immediately, even if the fire appears to be out, and close the lab door behind you on the way out.
  * From a safe location outside the building, wait for emergency responders and contact University Police at 412-268-2323 to report the incident.
  * Do not re-enter the building until cleared by emergency responders.
* Gas leak (UHP nitrogen carrier gas or pneumatic gas) as signaled by gas escape noise, loss of carrier gas flow, or loss of pneumatic gas pressure:
  * Hit the emergency power off button (closes valves and stops heating).
  * Close UHP Nitrogen carrier gas cylinder.
  * Close pneumatic gas valve (large white lever).
  * If the leak cannot be stopped or is major, evacuate the lab immediately, close the door behind you, and activate the building fire alarm pull station.
  * Notify the EHS and the lab manager once in a safe location. Do not re-enter until cleared by emergency responders.
* Loss of precursor exhaust flow as signaled by precursor box exhaust/vent line alarm:
  * Hit the emergency power off button (closes valves and stops heating).
  * Close UHP Nitrogen carrier gas cylinder.
  * Close pneumatic gas valve (large white lever).
  * Shut down the system and close all manual precursor ampoules valves.
  * Post a notice to alert other users not to operate the machine.
  * Notify EHS and the lab PI.

## Management of Changes to the ALD Chamber

The ALD chamber and the associated deposition process is inherently hazardous. This chamber in its current configuration has been reviewed by multiple stakeholders, including staff from the ECE Nanofabrication Lab and Environmental Health and Safety (EHS). Any changes to the equipment used in this research must be reviewed by the ECE Nanofabrication Lab and EHS before being implemented.

## ALD Recipe Execution Guidelines&#x20;

* Reference HfO2 ALD Cycle:
  * H₂O pulse (\~0.015 s)
  * N₂ purge (5–20 s)
  * Hf precursor pulse (0.15–0.40 s)
  * N₂ purge (5–20 s)
* Growth rate: \~1 Å/cycle
* Delivery line temperature: 150C
* Substrate temperature: 250C
* Precursor temperature: 75C&#x20;
* H2O precursor temperature: 20C&#x20;

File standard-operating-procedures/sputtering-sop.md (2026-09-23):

---
description: >-
  Guide to using the RF sputtering chamber. This is not a concise guide. You
  should understand the sputtering machine's design, function, and operating
  procedure well before interacting with it.
---

# Sputtering SOP

### Loading your chip and setting throw distance

1.  Put on nitrile gloves to prevent getting skin oils on or in the chamber and other equipment.

    <figure><figcaption></figcaption></figure>
2. Take the black frame from under the bench, and place it vertically in front of the chamber.&#x20;
3.  Wipe the top surface of the black frame with a clean room wipe to prevent transferring any contaminants to the top plate of the chamber.&#x20;

    <figure><figcaption></figcaption></figure>
4. Remove the top plate of the chamber and gently place it on the black frame, being careful to manage the gas lines and power lines attached to it.
5. To adjust the throw distance (distance between target and substrate), lift off the substrate plate and adjust the height of the 4 wing nuts used to support it.&#x20;
6. You can use a bubble level (located in the red bin below the bench) to ensure that the wings nut support the substrate plate in a flat plane.
7.  You can simply measure the distance between the substrate plate and target by using a ruler to look at the distance between the substrate plate and the top Viton gasket. The target surface sits 5/8" above the Viton gasket.&#x20;

    <figure><figcaption></figcaption></figure>
8.  Place your chip in the center of the substrate plate. &#x20;

    <figure><figcaption></figcaption></figure>
9. Place the top plate back onto the chamber, being careful not to introduce any contamination to the sealing surfaces.
10. Ensure the red alligator clip is grounding the top plate to the pump; it often unclips during the chip loading process.
11. Do not leave the top plate off for extended periods of time, as contaminates can accumulate in the chamber.

### Pumping down

1.  Ensure that the vent screw is hand tight. Do not over tighten.&#x20;

    <figure><figcaption></figcaption></figure>
2. Double check that both mass flow controllers are set to 0 SCCM.&#x20;
3.  On the digital control unit, use the arrows to scroll to parameter 707.

    <figure><figcaption></figcaption></figure>
4. Set parameter 707 to 100% by simultaneously clicking both areas, then using right arrow to select 100%, then simultaneously clicking both arrows to set it at 100%. This sets the pump speed to its maximum value of 1000 Hz.
5. Use the arrows to scroll to parameter 340, which displays the pressure in hPa. Parameter 309, the pump speed in Hz, should also be visible on the DCU.
6. As the pump spins up to 1000Hz, ensure that the pressure is decreasing. It should reach the E-4 to E-5 range within a few minutes. It should also steadily speed up to 1000 Hz without getting stuck at any speed. If either of these happen, then something is wrong; you need to double check all your seals and consider if anything in the chamber could be outgassing. For example - alumina has very low outgassing but is porous, so if you exposed it to water, then the water will evaporate out of the alumina over an extended period of time.
7. Once the pump has reached 1000Hz smoothly, and chamber pressure is in the E-5 hPa range, it is time to wait \~24 hours for the pump to reach base pressure. This system is capable of 1.5 E-7 hPa, but may not reach it due to contamination build up in the chamber or ion-sealing surfaces. Ensure that the chamber reaches <5E-7 hPa before proceeding; otherwise, your films will not be high quality, especially films like aluminum that are very reactive with oxygen or water vapor.

### Reaching striking pressure and sputtering pressure

1.  Open the argon cylinder all the way (lefty loosey!):&#x20;

    <figure><figcaption></figcaption></figure>
2. Ensure that the dual stage regulator has high pressure on the cylinder side and \~10-15 PSI on the chamber side.
3. On the Alicat mass flow controller, click the setpoint button, then use the select digit button, up button, and down button to set 10 SCCM. Hit the set button to actually begin flowing argon. Ensure that the MCF is flowing 10 +- .01 SCCM.
4. On the HiCube digital control unit, scroll to parameter 707.
5. Set parameter 707 to 100% by simultaneously clicking both areas, then using left arrow to select 25%, then simultaneously clicking both arrows to set it at 25%. This sets the pump speed to 250 Hz.
6. Use the arrows to scroll to parameter 340, which displays the pressure in hPa. Parameter 309, the pump speed, in Hz should also be visible on the DCU.
7.  Once the pump reaches 250Hz, it is time to make a map of flow rate and chamber pressure before striking plasma. This is necessary because when the plasma is on, the RF noise can disrupt the communication between the pressure gauge and digital control unit, giving inaccurate pressure readings. Do this by setting the MFC to various setpoints between 5 and 50 SCCM Ar. The chamber at CMU usually has the following flow-to-pressure relationship. If you're using O2, you can do this same process, but by adjusting the Ar and O2 flow rate simutlaneaously to ustain a constant O2:Ar flow ratio.

    | Flow SCCM | Pressure hPa |
    | --------- | ------------ |
    | 10        | 2.5E-3       |
    | 20        | 6.3E-3       |
    | 25        | 8.6E-3       |
    | 30        | 1.2E-2       |
    | 35        | 1.6E-2       |
    | 40        | 1.9E-2       |
    | 80        | 1E-1         |
8. Next, set Ar flow to approximately 80 sccm to achieve \~1E-1 hPa, which is the "striking pressure". Essentially, the electrical potential and pressure needed to strike a plasma are related through a non-monotonic curve, known as the Paschen curve. The goal is to strike the plasma at the minima of this curve. For our chamber, the minima of this curve has been experimentally determined to be near 1E-1 hPa.

### Striking the plasma, impedance matching, and depositing

1.  Ensure that the substrate shutter is in the blocking position.&#x20;

    <figure><figcaption></figcaption></figure>
2.  Double-check that the alligator clip is connecting the top and bottom.&#x20;

    <figure><figcaption></figcaption></figure>
3.  Switch on the switching DC power supply. This should also power on the radio and the antenna tuner.&#x20;

    <figure><figcaption></figcaption></figure>
4. Ensure the radio is set to 14 MHz.
5.  Turn the RF power on by taping the radio controller button down with a piece of tape as shown.&#x20;

    <figure><figcaption></figcaption></figure>
6. If the matching network has already been tuned for the target inside the chamber, then plasma will likely form immediately.
7.  If plasma does not form, you will need to adjust the TR tune knob until plasma does form.

    <figure><figcaption></figcaption></figure>
8. If plasma still is not striking, one of the following may be the issue: the pressure may be off, the magnetron and target may not be set right, or the ground and signal may be shorted.
9.  Once the plasma is formed, use the TR tune knob to fine-tune the matching. The goal is to get the forward power > 90 watts, and the reflected power <10 watts. They do not always add up to 100.&#x20;

    <figure><figcaption></figcaption></figure>
10. Lower to your selected sputtering pressure.
11. Carefully nudge the TR tune knob to fine-tune impedance matching again. If the plasma goes out, reset the Ar flow to \~80 SCCM, and repeat steps 1-10.
12. Note, the plasma is not always very stable below 1E-2 hPa.
13. Wait 15 minutes to ensure the target surface has been cleaned by the plasma bombardment. Then turn the shutter righty-tighty until it is no longer blocking the magnetron hole. When turning the shutter, avoid putting lateral force on it, as this could break the seal and ruin your sputtering run along with damaging the pump.&#x20;

    <figure><figcaption></figcaption></figure>
14. Wait the intended dwell time.

    <figure><figcaption></figcaption></figure>
15. Untape the radio controller to turn the plasma off.

### Shutting down and retrieving the chip

Basically do everything in reverse

1. Set both MFCs to 0 SCCM.
2.  Close both Ar and O2 cylinders (righty-tighty!).

    <figure><figcaption></figcaption></figure>
3. Turn off the pump.
4. Turn off the switching DC power supply.
5. Switch off all 3 fans.
6. Wait until the pump reaches 0 Hz.
7. Slowly unscrew the pump vent. No need to fully remove it.
8. Wait until chamber pressure reaches >1E-3 hPa.
9. Put the black frame on top of the table and set the top plate on it. It may difficult to remove the top plate. If so, grip the base of the pressure gauge and Ar MFC then tilt it off.
10. Retrieve your chip with tweezers.
11. Put the top plate back on.

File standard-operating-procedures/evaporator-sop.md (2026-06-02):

---
layout:
  width: default
  title:
    visible: true
  description:
    visible: true
  tableOfContents:
    visible: true
  outline:
    visible: true
  pagination:
    visible: false
  metadata:
    visible: true
  tags:
    visible: true
  actions:
    visible: true
---

# MTI Evaporator SOP (No longer in use)

<figure><figcaption><p>Before Evaporation </p></figcaption></figure>

<figure><figcaption><p>Post Evaporation (Aluminum in Blue)</p></figcaption></figure>

***

## Parameters

| Bakeout Time                                                |             |
| ----------------------------------------------------------- | ----------- |
| Pressure Before Beggining Evaporation (hPa)                 | <p><br></p> |
| <p>Temp Time Sequence [c1, t1, c2, t2, c3, t3, ...]<br></p> | <p><br></p> |

## Purpose



Figure from Microchip Fabrication (Van Zant, 2004)

Thermal evaporation is a layer deposition technique wherein the vapor pressure of a material is increased via resistive heating while the surrounding air is evacuated below that vapor pressure. The [mean free path](https://www.pfeiffer-vacuum.com/en/know-how/introduction-to-vacuum-technology/fundamentals/mean-free-path/) of gas in the chamber, which is determined by the pressure, must also be larger than the source to substrate distance. Under these conditions, the material evaporates into the vacuum and then coats any exposed surfaces. This is how we create deposit layers of metal, which are later etched into wires, and contact pads.

The Hacker Fab currently uses aluminum for wiring because it’s relatively conductive, fast to evaporate, and cheap. However, it can be tricky to evaporate because it alloys readily with many refractory metals. This is described in depth [here](https://www.lesker.com/newweb/deposition_materials/deposition-materials-notes.cfm?pgid=al1). We currently use an alumina crucible which seems to work for a handful of evaporations, though other setups may be more effective and should be tested.

***

## Tools

1. MTI Thermal Evaporator with Inficon Film Thickness Monitor

## Materials

1. Kapton tape
2. 99.999% Aluminum wire
3. Recommended: piranha solution

***

## Procedure

### Preparation

1. Open the [Evaporation Data](https://docs.google.com/spreadsheets/d/1pLmIeejaP6-JWRBXLnWrWZQuf21_CxsJdZeJoiU9y5w/edit?usp=sharing) sheet and plan your experiment.
2. (Recommended) Use piranha solution or [O2 plasma](https://docs.google.com/document/d/18O1M_P8trr4wdzKeulmmXW6kANNKmp0MQrCSmAgrgFM/edit?usp=sharing) to clean the chip.
3. Place the chip on a hot plate at 180°C for 90 minutes. Cover it to avoid surface contamination.
4. Wear gloves while handling parts exposed to vacuum because oil from your hands will outgas.
5. Use double sided kapton tape to attach the chip(s) to the center of the substrate holder.
6. Put 20 cm of aluminum wire into the crucible.

### Bakeout

1. Use double sided kapton tape to attach the chip(s) to the center of the substrate holder.
2. Carefully close the chamber.
3. Check that the vent knob on the turbopump is fully closed by turning clockwise.
4. Start the vacuum by pressing the on/off button on the pump.



5. Program the bakeout sequence to ramp to 700°C over 2000 s, then hold for 3600 s, then ramp down over 2000 s. Refer to page 15 of the [evaporator manual](https://drive.google.com/file/d/163nug7sO17XjpK8Gmx-9_C81ZMmk-d6B/view?usp=share_link) for detailed programming instructions.&#x20;
6. Wait for the pressure to get below 5E-5 hPa. You can also program the bakeout to have a long 0°C segment at the beginning.
7. Make sure that the current knob on the side of the evaporator is in the “Auto” position.
8. Press “Set” and “◀” to return to the standby state, then press and hold “▼” for 2 seconds to start the program. Press the green run button to enable current flow.

### Evaporation

1. Ensure the pressure reads less than 5E-6 hPa.&#x20;
2. Program the evaporator to ramp to 1125°C over 2000 seconds, hold for 500 seconds, and ramp down over 2000 seconds.
3. Start the program. Set a timer for 28 minutes so that you open the shutter at the right time.
4. Set up the film thickness monitor by plugging its USB cable into the laptop and starting the STM-2 software.
5. When the evaporator reaches the target temperature, open the shutter using the knob at the top of the chamber and press “zero” on the STM-2 software.
6. Monitor and record the pressure (should be below 5E-6 hPa) and deposition rate (should be greater than 5 Å/s) during the evaporation.
7. When the temperature starts to drop, close the shutter.
8. Wait for the temperature to drop below 350°C before proceeding

### Vent

1. Turn off the pump by pressing the same on/off button.
2. Wait 10 minutes for the turbopump blades to slow down.&#x20;
3. Slowly turn the knob on the turbopump until the pressure starts to increase (<¼ turn). Don’t open it all the way or the rapid pressure increase will destroy the pump, which is still spinning really fast.&#x20;
4. Wait another 10 minutes.
5. Once the pressure has increased to 1 hPa, open the valve a bit more. Wait until the chamber is at 1000 hPa (1 bar).
6. Open the chamber and place the substrate holder face up.
7. Use a utility knife blade to separate the chip(s) from the substrate holder.
8. Peel/scrape off any tape residue left on the chip.
9. Take inspection pictures and upload them in a new [Evaporation Photos](https://drive.google.com/drive/folders/1UahZeNBUPMZiq7Gocv0FQa7C8czsouz5?usp=share_link) folder, then link that folder in the [Evaporation Data](https://docs.google.com/spreadsheets/d/1pLmIeejaP6-JWRBXLnWrWZQuf21_CxsJdZeJoiU9y5w/edit?usp=sharing) spreadsheet.

### Anneal

400-500C

***

## Safety

1. As previously mentioned, don’t vent the chamber too quickly. Turbopumps supposedly have the kinetic energy of a car on a highway and can “grenade”... we don’t want to find out what that means.
2. The sample holder may be hot. Be careful.

## Appendix

## Flash Evaporation Alternate Technique

Use this as a backup technique when the crucible/thermocouple are out of commission. No temperature control is used, instead we manually control the current running through a tungsten filament with aluminum wire wrapped around it. This is a quicker, less accurate technique. The deposition monitor can still be used to determine when the metal is depositing on the chip, though it may be less accurate due to the rate of deposition.

### Preparation

1. Use a 3-wire tungsten filament instead of a crucible. Wrap 20 cm of aluminum wire around it, keeping away from either end.
2. Screw it into the terminal posts in the evaporator.
3. Scrape/wipe off some deposited aluminum from the glass jar so that you can see into the chamber.
4. Follow all other steps for pump down, except anything that mentions programming temperatures.

### Evaporation

1. Turn the switch on the right of the machine clockwise so it's set to manual mode.
2. Use the knob above it to set current to 12A. The current is displayed on the front panel.
3. Monitor the filament for \~5 minutes until it starts to glow. The aluminum will also melt and wet onto the filament.
4. Increase the current to \~20A. It should start to glow white hot. If the deposition monitor is on, it should start to record some deposition. The walls of the chamber will also turn opaque from the aluminum. Hold for a couple minutes.
5. Decrease the current to 10A, then 5A, then 0A to slowly cool the filament. Wait 10 minutes.
6. Follow the vent procedure listed above.

***

<br>

Misc. notes that need to be organized:

Manually switch to evaporation procedure (based on evaporation data spreadsheet, using thickness monitor to determine when to stop)

Sam only evaporated for 1 minute, we are doing \~15?

Let it evaporate at 1100 for 3 min before moving guard to expose chip

This is because there is scum in the crucible and might be oxygen in the chamber at the beginning of evaporation that causes aluminum oxide to build on chip

<br>

1. Evaporation is faster than sputtering (supposedly, it might be equivalent because evaporation operates at a much lower pressure than sputtering so pump down and bakeout take a whi

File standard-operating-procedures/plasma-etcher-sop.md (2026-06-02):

---
description: This SOP is specifically for etching 300nm of polysilicon in the NMOS process
layout:
  width: default
  title:
    visible: true
  description:
    visible: true
  tableOfContents:
    visible: true
  outline:
    visible: true
  pagination:
    visible: false
  metadata:
    visible: true
  tags:
    visible: true
  actions:
    visible: true
---

# Plasma Etcher SOP

<figure><figcaption><p>Before Reactive Ion Etch (RIE)</p></figcaption></figure>

<figure><figcaption><p>After Reactive Ion Etch (RIE)</p></figcaption></figure>

## Parameters

| Total Time    | 15 min  |
| ------------- | ------- |
| SF6 flow rate | 10 sccm |
| Etch time     | 60s     |
| RF Power      | 100W    |

#### For more detaild process parameters:

[Plasma Etch Process Sheet](https://docs.google.com/spreadsheets/d/1-mvhaMWhcO-PKCisJJNyvKJd4Pv3DMQQeegNJ-yXHSk/edit#gid=0)

[Plasma Clean Process Sheet](https://docs.google.com/spreadsheets/d/1n-9ACh263syzrxcAJIWBtZ5d4DbPKWw7ZwvzPnsIGhM/edit#gid=0)

***

## Purpose

This first etch step creates the transistor’s gate by etching away almost all of the polysilicon and gate oxide, except for the islands covered by patterned photoresist. We use plasma etching (AKA dry etching) for two reasons:

1. Plasma is capable of etching silicon, whereas HF is not.
2. The anisotropic (vertical) etch profile is capable of transferring smaller patterns than isotropic etches.



The plasma etcher breaks down the normally inert SF6, creating a fluorine ion containing plasma on the surface of the chip. A combination of physical bombardment and chemical reaction removes material from the surface. Physical bombardment occurs when the pressure is low (<\~.1 Torr) and results in an anisotropic (vertical) etch. This allows for precise transfer of a photoresist pattern onto the underlying material. Chemical etching dominates at higher pressures and results in an isotropic etch. Fluorine reacts more quickly with Si than SiO2, resulting in high selectivity.

***

## Tools

1. PE-25 Plasma Etcher

## Materials

1. Chip with patterned resist on Si
2. Acetone
3. Isopropanol

***

## Procedure

### Preparation

1. If you have already claimed a chip number, and opened its specific chip view data sheet, record your patterning data into that sheet. If you have NOT claimed a chip number, and have NOT begun recording data in a chip specific sheet, open this [central chip count](https://docs.google.com/spreadsheets/d/1MrqtnkHcNr5hekHpQHusBZJG4nrdcxDz7Yg5Emn9BMQ/edit#gid=0) sheet, claim the next available chip number, open the blank chip view sheet for that specific chip number and record all subsequent process data into it.
2. Turn on the etcher via the switch on the back panel.
3. Turn on the laptop and open the Plasma Etch app.
4. Turn on the RF power supply on top of the etcher.
5. Open the chamber and place your chip in the middle of the rack. Close the chamber.
6. Set O2 flow, SF6 flow, power, time, vacuum setpoint in Sequence screen. Save your sequence.

### Etching

1. At the top menu bar, go to **power** and turn on RF and vacuum. The pump will start.
2. Wait until the pressure (the number next to "vacuum") is below .1 Torr.
3. Go to **commands > cycle off**. This will purge the chamber for three seconds with nitrogen in order to remove H2O. If any water is in the chamber during the plasma it will react with fluorine to make HF. Very bad.
4. **Commands > standby**. This will start the pump again.
5. Repeat steps 2-4 to purge again. This makes sure no water is in the chamber.
6. Open the valve on the cylinders of gas that you are using. Lefty loosey.



7. When you are ready to start etching, select **commands > plasma**.&#x20;
8. During the etch, monitor the pressure on the screen (should be at your setpoint) and the outlet pressure on the regulator (should be around 5-15 psig). Look in the window for pretty plasma!
9. SHUT THE GAS CYLINDER. RIGHTY TIGHTY
10. At the end of the cycle, the etcher will purge itself once, pump down, then purge again. To be safe we’ll purge a third time:
11. **Commands > standby**. This will start the pump again.
12. Wait until the pressure is below .1 Torr.
13. **Commands > cycle off**. Lets gas in for 3 seconds
14. **Commands > standby**.
15. Wait until the pressure is below .1 Torr.
16. **Commands > shutdown**. The chamber will come to atmosphere in 30 seconds, at which point you can open it.

## O2 Plasma Cleaning

The procedure is the same as for silicon etching, but you may skip a purge before and after the plasma. This is because&#x20;

| Total Time   | 6 min   |
| ------------ | ------- |
| O2 flow rate | 10 sccm |
| Etch time    | 120s    |
| RF Power     | 100W    |

***

## Safety

SF6 is not toxic, but fluorine is. By purging before and after the plasma, we’re trying to prevent two things:

1. Purging before removes all water from the chamber. This prevents any HF from being formed, which would otherwise corrode the pump and exhaust. If the exhaust hose connected to the pump turns green, this is an indication that HF is being formed.
2. Purging after removes all reaction products from the chamber. This includes SiF4 and various other sulfur oxides.

<br>

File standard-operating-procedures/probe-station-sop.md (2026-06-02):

---
layout:
  width: default
  title:
    visible: true
  description:
    visible: true
  tableOfContents:
    visible: true
  outline:
    visible: true
  pagination:
    visible: false
  metadata:
    visible: true
  tags:
    visible: true
  actions:
    visible: true
---

# Probe Station SOP

## Purpose

After fabrication, the chip must be tested to demonstrate the functionality of the design. Additionally, variations and errors in fabrication may result in differences in device characteristics which are useful to document when these variations cause the device to fail.

To enable precisely controlled experiments on microscopic chips, we currently use a probe station to contact the device using sharp probes which supply and measure voltages for calculation of various device characteristics such as I-V curves, which are explained in this SOP.

## Tools

* Probe station setup
  * Probe station - Karl Suss PM5
  * At least 4 probes, manipulators, and coaxial cables
* Microscope setup
  * Camera - AmScope MU1000-HS and AmScope viewing software
  * Light – MI-150 Fiber Optic Illuminator
* Keithley semiconductor analyzer system
  * Keithley 4200-SCS Semiconductor Parameter Analyzer
  * Keithley 2636a Sourcemeter
  * Keyboard and mouse

## Materials

* Devices under test – typically a finished chip with pads for probing
* Computer running [AmScope viewer software](https://amscope.com/pages/software-downloads)
* Flash drive for data transfer

## Procedure

### General setup and cleanup



1. Place the chip in the center of the stage and turn on the vacuum.
2. Turn on the microscope light, which appears as a spot of light on the stage.
3. Connect the microscope camera to your computer and select the camera MU-1000HS on the AmScope viewer software, which should summon the camera view. The Keithley semiconductor analyzer has only two USB ports, which are currently occupied by a keyboard and mouse. Without WiFi or a USB hub, the camera view and data transfer are handled by another computer.
4. Turn on the Keithley semiconductor parameter analyzer.
5. Open the **KITE software** and the experiment of interest (see below sections).
6. Using coaxial cables and connectors, connect each probe to the corresponding port on the Keithley semiconductor parameter analyzer.
7. Raise the stage using the lever. Focus the stage and center the pattern of interest under the light source using the knobs below the stage.
8. If the probe tips are not illuminated by the microscope light, carefully move the magnetically-attached manipulators such that the range of motion of the probe tips is within the spot of light.
9. Using the knobs on each probe’s manipulator, lower the probes so that the tips are focused yet not touching the chip, then position the probe tips above their corresponding probing pads.
10. Carefully lower the probe tips to touch the pads, which is generally indicated by resistance to movement when attempting to lower the tip further. The manual nature of this process means that the sharp probes can scratch the chip and damage the device beyond future usage, such as scratching the pads off.
11. Press the green triangle in the KITE software to run the experiment.
12. Once the experiment finishes, check the data for errors and repeat the experiment as necessary.

 

13. Scale the graph such as by right clicking the graph and clicking `Autoscale` and save the data in a folder named `chip###` where `###` is the chip number. To save the graph and data with a common name, type the name and click `Populate`, `Save All`, then `Exit`.
14. Remove the probes from the chip and continue to the next device, either by lifting the probes or lowering the stage.
15. After all experiments are finished, transfer the data to a flash drive and upload the data (such as to Google Drive).
16. Raise the probes using the manipulator knobs.
17. Lower the stage by turning the lever.
18. Turn off the Keithley parameter analyzer.
19. Disconnect the microscope from your computer and turn off the microscope light.
20. Turn off the vacuum and remove the chip.

### MOSFET I-V Curve



1. Upon opening the KITE software, choose the `vds-id test` from under the section `4terminal-n-fet`.
2. Configure the probes and measurements using the following parameters. Make sure that the correct coaxial cable (SMU1, SMU2, GNDU) is connected to the correct probe.

| Parameter     | Value |
| ------------- | ----- |
| Vds range     | 0-10V |
| Vds step size | .1V   |
| Vgs range     | 0-5V  |
| Vgs step size | 1V    |
| Vb range      | 0     |
| Vb step size  | n/a   |

3. The I-V curve of the MOSFET and the gate leakage current should be plotted. Note the magnitude of the voltage and current measurements. Very low current in the range of nano-amperes or below can indicate an open circuit, and linear behavior can indicate a short circuit, which can arise from a fault in the device or improper probe placement.

### Gate & Contact Resistance



1. Upon opening the KITE software, chose the `res2t` test froom under the section `2-wireresistor`.
2. Configure the probes and measurements using the following parameters. Make sure that the correct coaxial cable (SMU1, SMU2) is connected to the correct probe.

| Parameter   | Value |
| ----------- | ----- |
| V range     | +-5V  |
| V step size | <=1V  |
| Vgs range   | 0-5V  |

3. The I-V relationship between the two probes and resistance estimated from Ohm’s law should be plotted. An ideal resistor should have a linear relationship and constant resistance.

***

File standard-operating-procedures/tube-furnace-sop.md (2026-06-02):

---
layout:
  width: default
  title:
    visible: true
  description:
    visible: true
  tableOfContents:
    visible: true
  outline:
    visible: true
  pagination:
    visible: false
  metadata:
    visible: true
  tags:
    visible: true
  actions:
    visible: true
---

# Tube Furnace SOP

<figure><figcaption><p>Doped Silicon (grey) and Doped Gate Poly (dark blue) Resulting from Thermal Diffusion</p></figcaption></figure>

<figure><figcaption><p>Tube Furnace</p></figcaption></figure>

## Parameters

| Temperature    | generally 1100°C                                   |
| -------------- | -------------------------------------------------- |
| Diffusion time | generally 30 min for defining source/drain regions |

***

## Purpose

The primary use of the tube furnace is for diffusion of dopant atoms into silicon. The incorpoation of dopant atoms into the Si lattice creates defects in the electronic structure, which are charge carriers, increasing the conductivity of the diffused region and making it either N or P type. Diffusion of a solid into another solid is quite slow, so high temperatures and long times are needed, hence the high-temperature tube furnace.

Our process uses spin on glass containing phosphorus for N doping and boron for P doping.

***

## Tools

1. Tube Furnace ([ThermoFisher Manual](https://drive.google.com/file/d/1ZI5JLqLPNKlWIGWCSD1lCgYlSFpEnkOj/view?usp=sharing)) with Quartz tube
2. Quartz rod
3. Quartz microscope slide, or Fused silica boat

## Materials

1. Chip with glass containing phosphorus or boron.

***

## Procedure

### Pre-heating the Furnace

1. Turn on the furnace.&#x20;
2. Press and hold “set/ent” for three seconds until “mode res” is showing. Press the up arrow twice until mode “LCL” is selected. Press “enter” once. Now the furnace will hold the temperature shown. Use the arrow keys to adjust and press “enter” once to set the setpoint.&#x20;
3. If the furnace stops and holds at a lower temperature than your setpoint, the high temperature alarm may be too low. Read the instructions on [page 6-7](https://drive.google.com/file/d/1ZI5JLqLPNKlWIGWCSD1lCgYlSFpEnkOj/view?usp=sharing) to fix this.

### Inserting chips



1. Put the Quartz microscope slide in the entrance of the tube. Do not use a regular borosilicate microscope slide, or it will melt inside the tube. The edge of a fused silica slide is pure white, while borosilicate is a little bit green.

<figure><figcaption><p>Differentiating Quartz from Borosilicate</p></figcaption></figure>



_A chip permanently fused to the tube furnace walls when improper slide was used_ :fire:

1. Place your chips on the slide.
2. Put on the heat resistant gloves.
3. Use the glass rod to push the slide into the center tube, being careful to not scratch the inside of the tube too much
   1. Measure out how far the glass rod needs to be pushed in to place the chips atthe center of the tube furnace.
4. The rod is extremely hot, and will auto ignite what it touches, or burn through flesh. carefully place it a top the tube furnace

### Removing chips

1. Use the glass rod to push the slide to the other end of the tube.
2. Wait a few minutes for the slide to cool down.
3. Use metal tweezers to take the slide out. place it on the upside down beaker to allow it to cool further
4. Wait 3 minutes before handling the chip.

***

## Safety

The furnace is obviously very hot. Keep away from any hot parts of the furnace. The rod will heat up in the few seconds that it is inside the tube, so when removing it, only hold it by the colder end.

The rod and tube also channel heat out of their ends via internal reflection of radiation.

<br>

***

<br>

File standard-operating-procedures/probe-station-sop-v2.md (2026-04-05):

---
description: Version 2 of the probe station using analog discovery 3s
---

# Probe Station SOP - V2

## Purpose

After fabrication, the chip must be tested to demonstrate the functionality of the design. Additionally, variations and errors in fabrication may result in differences in device characteristics which are useful to document when these variations cause the device to fail.

To enable precisely controlled experiments on microscopic chips, we currently use a probe station to contact the device using sharp probes which supply and measure voltages for calculation of various device characteristics such as I-V curves, which are explained in this SOP.

## Tools

* Probe station setup
  * Probe station - Karl Suss PM5
  * At least 4 probes, manipulators, and coaxial to split jumper wires with hooks at the end
* Microscope setup
  * Camera - AmScope MU1000-HS and AmScope viewing software
  * Light – MI-150 Fiber Optic Illuminator
* Semiconductor analyzer system
  * 2 Analog Discovery 3s
  * Laptop with ability to connect to camera and analog discovery 3s as well as run a python program

## Materials

* Devices under test – typically a finished chip with pads for probing
* Computer running [AmScope viewer software](https://amscope.com/pages/software-downloads) and Python program

## Procedure

### Setup



1. Place the chip in the center of the stage and turn on the vacuum.
2. Turn on the microscope light, which appears as a spot of light on the stage.
3. Connect the microscope camera to your computer and select the camera MU-1000HS on the AmScope viewer software, which should summon the camera view.&#x20;
4. Open the analyzing software on a laptop
5. Raise the stage using the lever. Focus the stage and center the pattern of interest under the light source using the knobs below the stage.
6. If the probe tips are not illuminated by the microscope light, carefully move the magnetically-attached manipulators such that the range of motion of the probe tips is within the spot of light.
7. Using the knobs on each probe’s manipulator, lower the probes so that the tips are focused yet not touching the chip, then position the probe tips above their corresponding probing pads.
8. Carefully lower the probe tips to touch the pads, which is generally indicated by resistance to movement when attempting to lower the tip further. The manual nature of this process means that the sharp probes can scratch the chip and damage the device beyond future usage, such as scratching the pads off.
9. Using coaxial cables connected to the jumper wires with hooks, connect each probe to the ground, source, and drain on the Keithley and connect the corresponding red hooks to the equivalent ground, source, and drain pins on the circuit board as well as all the black hooks to the drain pin on the circuit board like in the below picture

<figure><figcaption></figcaption></figure>

### Run Program

<figure><figcaption><p>Program from Vscode view + terminal</p></figcaption></figure>

<figure><figcaption><p>New window with plot of IV curves for ideal mosfet</p></figcaption></figure>

1. Run the command python3 smu.py in terminal to run the program
2. This will open up a new window with a plot of the IV Curve that looks something the below picture under MOSFET I-V Curve
3. In order to close this window and continue with the program, either hit the red exit button on the image window or go to terminal and type Ctrl-C
4. If the graph had errors, repeat the experiment as necessary
5. If the data looks good, enter the title for the current and image csv files

### Cleanup

1. Remove the probes from the chip and continue to the next device, either by lifting the probes or lowering the stage.
2. Raise the probes using the manipulator knobs.
3. Lower the stage by turning the lever.
4. Disconnect the microscope from your computer and turn off the microscope light.
5. Turn off the vacuum and remove the chip.

### MOSFET I-V Curve

The outputs currently look something like this:

<figure><figcaption><p>IV Curves for Chip 234 with Gate Voltages of 1, 2, 3, 4, and 5 Volts</p></figcaption></figure>

The I-V relationship between the two probes and resistance estimated from Ohm’s law should be plotted. An ideal resistor should have a linear relationship and constant resistance.

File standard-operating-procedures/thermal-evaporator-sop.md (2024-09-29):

---
layout:
  title:
    visible: true
  description:
    visible: true
  tableOfContents:
    visible: true
  outline:
    visible: true
  pagination:
    visible: false
---

# Thermal Evaporator SOP

***

## Purpose

Thermal evaporation heats up a metal (in this case Aluminum) to really hot temperatures in order to evaporate it onto the chip. Evaporating metals like aluminum is what allows us to conduct electricity through our design.

***

## Procedure

1. Make sure the vacuum has been turned off for at least 5 minutes
2. Make sure pressure is at room pressure (~1000 hPa) as shown in Figure 2. If it is not, slowly open the valve (black knob on the right side of the vacuum) as shown in Figure 3, and release pressure one order of magnitude about every 15 seconds
3. Turn the two black knobs on the top of the blue box as shown in Figure 2, and open the lid
4. Unscrew any screws holding down the Tungsten coil as shown in Figure 5, and remove the coil
5. Tightly wrap aluminum around the Tungsten coil. This alloy is brittle so be careful and don't wrap too tightly if you have less aluminum you need to evaporate
6. Place Tungsten back and screw it in. Make sure it is straight
7. Put the yellow tape on the square box attached to the inside of the lid as shown in Figure 4, then peel off the clear layer on top of the tape
- Since aluminum often covers the square box, when you put the tape on, aluminum might stick to it and flake off and so you might lose grip. If the tape isn't sticking because of this, just do it again
8. Put your chip on the yellow tape as shown in Figure 4
9. Double check that the metal sheet at the back is not bent and still covering the vacuum as shown in Figure 5
10. Close the blue lid and screw the black knobs all the way
11. Close the vent all the way
12. Turn on the pump as shown in Figure 2
13. Screw the black knobs more since they tend to loosen after the pump turns on
14. Wait for the pressure on the screen to get under 1e-5 hPa as shown in Figure 2. This will take 30 min - 1 hr depending on how clean the inside of the chamber is (Baking the chips and trying not to touch the inside of the chamber too much will help speed this up)
15. Turn on the power source as shown in Figure 1
16. Press start on the computer as shown in Figure 1
17. Turn up the current on the power source as shown in Figure 1. Keep adjusting the current to keep the rate between 30-100 Angstroms/second until the thickness hits 5 Angstroms
- If you click the dial, you can change the digit.
- You will probably end up between 40-50 Amps. 
- The voltage and power will automatically change as you adjust the current so you do not need to worry about it.
- The pressure might increase to 1e-4 which is not a problem
- You may not get to 5 Angstroms so keep turning up the current but after 5 minutes, if you keep increasing past 55 Amps and it does not increase, the aluminum has probably already melted off. It is not a huge deal if the layer is thin but it is not ideal
18. After the thickness hits 5 Angstroms, turn off the power source
19. Press stop on the computer program
20. Turn off the vacuum pump. WAIT at least 5 minutes
21. After 5 minutes, slowly open the valve (black knob on the right side of the vacuum) and release pressure one order of magnitude about every 15 seconds

***

## Figures


<br />
<i>Figure 1: Program on computer next to thermal evaporator, Note green start button to start, rate (A/s) in the table, and thickness (Angstroms) in the table on the computer program. A (yellow circle) indicates the power supply on bottun and B (red circle) indicates the knob for adjusting current. </i>
<br />
<br />

<br />
<i>Figure 2: Front of thermal evaporator. A (red circle) indicates the screen which shows pressure while B (blue circles) indicates the lid's knobs and C (yellow circle) indicates the vacuum on/off button </i>
<br />
<br />

<br />
<i>Figure 3: Right side of thermal evaporator. A (blue circle) indicates the knob to close and open the vent </i>
<br />
<br />

<br />
<i>Figure 4: Thermal evaporator with lid open. A (red circle) indicates where the tape and chip should be placed </i>
<br />
<br />

<br />
<i>Figure 5: Inside of thermal evaporator. A (red circle) indicates the Tungsten coil, B (blue circles) screw the coil in place, and C (yelow circle) is the metal sheet blocking the vacuum </i>

***

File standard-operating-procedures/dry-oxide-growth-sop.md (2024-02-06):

---
description: SOP for dry oxide growth of 10nm SiO2
---

# Dry Oxide Growth SOP

<figure><figcaption><p>Silicon before and after oxidation</p></figcaption></figure>

## Parameters

| Temperature | 1100°C                     |
| ----------- | -------------------------- |
| Total Time  | 30 min (subject to change) |

## Purpose

The oxidation growth of the silicon layer creates a layer of insulation to prevent direct flow from the conducting MOSFET layer to the metal gate.

1. Tube Furnace ([ThermoFisher Manual](https://drive.google.com/file/d/1ZI5JLqLPNKlWIGWCSD1lCgYlSFpEnkOj/view?usp=sharing)) with fused silica tube
2. Fused silica rod
3. Fused silica microscope slide

## Tools

1. Tube Furnace ([ThermoFisher Manual](https://drive.google.com/file/d/1ZI5JLqLPNKlWIGWCSD1lCgYlSFpEnkOj/view)) with fused silica tube
2. Fused silica rod
3. Fused silica microscope slide

## Materials

1. Pure silicon chip (not pre-deposited)

## Procedure

### Pre-heating the Furnace

1. Turn on the furnace.
2. Press and hold “set/ent” for three seconds until “mode res” is showing. Press the up arrow twice until mode “LCL” is selected. Press “enter” once. Now the furnace will hold the temperature shown. Use the arrow keys to adjust and press “enter” once to set the setpoint.
3. Wait \~15 min for the furnace to come to temperature.
4. If the furnace stops and holds at a lower temperature than your setpoint, the high temperature alarm may be too low. Read the instructions on [page 6-7](https://drive.google.com/file/d/1ZI5JLqLPNKlWIGWCSD1lCgYlSFpEnkOj/view) to fix this.

### Inserting chips

<figure><figcaption></figcaption></figure>

1. Put the <mark style="background-color:yellow;">fused silica</mark> microscope slide in the entrance of the tube. Do not use a regular borosilicate microscope slide, or it will melt inside the tube. The edge of a fused silica slide is pure white, while borosilicate is a little bit green.

<figure><figcaption></figcaption></figure>

_A chip permanently fused to the tube furnace walls when improper slide was used_ :fire:

1. Place your chips on the slide.
2. Use the glass rod to push the slide into the center of the tube, being careful to not scratch the inside of the tube too much.  Start the timer.&#x20;
3. Place the rod on top of the tube furnace (it will be hot).

### Removing chips

1. Use the glass rod to push the slide to the other end of the tube.&#x20;
   1. Push the slide all the way to the end until it is reachable.
   2. Put the rod on top of the tube furnace (it will be hot).
2. Wait a few minutes for the slide to cool down.
3. Use metal tweezers to take the slide out. Don't use the orange ones because they don't close all the way.
4. Put the slide on a heat resistant surface and wait 5 minutes before handling the chip.

## Safety

The furnace is obviously very hot. Keep away from any hot parts of the furnace. The rod will heat up in the few seconds that it is inside the tube, so when removing it, only hold it by the end.

The rod and tube also channel heat out of their ends via internal reflection of radiation.

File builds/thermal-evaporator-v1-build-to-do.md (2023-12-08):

# 💡 Thermal Evaporator V1 Build (to do)

## Vacuum Chamber Assembly

After purchasing and receiving all parts outlined in the [Evaporator Bill of Materials](https://docs.google.com/spreadsheets/d/1TPauRe4IT71wgZRzCAktdQAIhP94O9i4d5mw1youb1I/edit?usp=sharing), follow the step-by-step process to assemble the vacuum chamber.

#### 1. Assemble the chamber frame and plates

<figure><figcaption><p>Aluminum Frame</p></figcaption></figure>

<figure><figcaption><p>Plate with O-Ring</p></figcaption></figure>

(i) Wrap an O-ring around each plate to ensure the chamber has a tight vacuum seal.

<figure><figcaption><p>Plate with 8 bolts</p></figcaption></figure>

(ii) Screw in each plate with 8 bolts into the frame as shown in the following image.

_Note: Plan where you want each plate to be (i.e. top, bottom, side) depending on your setup_

<figure><figcaption><p>Screw in bolts to attach plate to frame</p></figcaption></figure>

#### 2. Attach feedthroughs and/or blank flanges

Each opening must be covered and sealed for the vacuum to exist. Therefore, each opening needs a feedthrough in it or a blank flange to cover it. Ensure that each part has the correct dimension to properly fit in its corresponding port.

(i) Pair up the feedthrough/flange with its matching O-ring and clamp.

<figure><figcaption><p>KF-16 viton ring and blank flange</p></figcaption></figure>

(ii) Layer the parts in the following order. Starting from the bottom closest to the plate place the O-ring, flange/feedthrough, and clamp. Then attach all necessary screws tightly. Repeat this process for all openings.

<figure><figcaption><p>Attaching a blank flange to a KF-16 port</p></figcaption></figure>

#### 3. Turn a face into a door and attach feet

(i) Screw in the hinge into two adjacent plates where you want the door to be.

<figure><figcaption><p>Hinge to allow top face to open</p></figcaption></figure>

(ii) Attach knobs on opposite side of hinge to open and close the door securely.

<figure><figcaption><p>Plate with hinge and knobs</p></figcaption></figure>

(iii) Attach feet to the bottom of the chamber to minimize vibration.

<figure><figcaption><p>Attaching rubber feet to chamber</p></figcaption></figure>

#### Final product

<figure><figcaption><p>Fully assembled vacuum chamber</p></figcaption></figure>

## Pumping down the Vacuum Chamber

#### 1. Attach the turbo pump to the chamber

Connect the turbo pump (Hi-Cube 80) to the KF-40 plate using the corresponding KF-40 flange and O-ring. Since the turbo pump has a lip that makes it difficult to tighten the screws, we recommend using hex shaped 10-32 x 5/8" screws and tightening with a wrench.

#### 2. Connect the pressure gauge

The Pfeiffer MPT 200 Gauge has a KF-25 connection port. To optimize the 6 plates we chose, an adapter from KF-25 to KF-16 is needed to connect the pressure gauge to the vacuum chamber. Attach using a KF-16 flange to the plate and a KF-25 clamp to connect the adapter to the pressure gauge.

<figure><figcaption><p>Vacuum chamber connected to turbo pump.</p></figcaption></figure>

## Implement Heating Parts

Heating the vacuum chamber is necessary for two reasons. First, high temperatures of approximately 1200˚C are needed to evaporate the aluminum and perform the thermal evaporation process. Second, heating the chamber allows it to bakeout, meaning that the water trapped inside evaporates allowing the vacuum to achieve a lower pressure.

Our setup consists of two parts: the **crucible** and the **substrate heater.**

### Crucible Set-Up

The crucible is comprised of the following parts:

* #### [Tungsten Filament](https://www.lesker.com/newweb/evaporation\_sources/basket-crucible-heaters.cfm)
* #### [Alumina Thermal Crucible](https://www.lesker.com/newweb/evaporation\_sources/thermal-crucibles-alumina.cfm?highlight=EVC1AO)
* #### [Insulating Bucket](https://www.lesker.com/newweb/evaporation\_sources/thermal-crucibles-alumina.cfm?highlight=EVC5AO\&highlight=EVC5AO)

After assembling these parts together, connect the copper power feedthroughs to either end of the tungsten filament using an [inline barrel connector](https://www.lesker.com/feedthroughs/connectors-inlinebarrel/part/ftaibc094).

[Ceramic beads](https://www.lesker.com/newweb/feedthroughs/ceramic\_fishsplinebeads.cfm?pgid=0) can be used to safely insulate the metal and prevent electrical misconnections.&#x20;

Next, connect a power supply to the external end of the power feedthroughs to heat up the crucible.

Finally, attach the thermal  breakout board and arduino to the thermocouple to read the temperature values.&#x20;

<figure><figcaption><p>Crucible heated to evaporate aluminum and deposit over chip.</p></figcaption></figure>

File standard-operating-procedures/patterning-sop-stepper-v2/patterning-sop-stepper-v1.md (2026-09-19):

---
layout:
  width: default
  title:
    visible: true
  description:
    visible: true
  tableOfContents:
    visible: true
  outline:
    visible: true
  pagination:
    visible: false
  metadata:
    visible: true
  tags:
    visible: true
  actions:
    visible: true
  anchors:
    visible: true
---

# Patterning SOP - Stepper V1

<figure><figcaption><p>Generic Patterning Sequence</p></figcaption></figure>

## Parameters

<table><thead><tr><th width="262"></th><th width="116"></th><th width="213"></th><th></th></tr></thead><tbody><tr><td>HMDS Prebake Temperature</td><td>100°C</td><td>Resist Bake Temperature</td><td>100°C</td></tr><tr><td>HMDS Prebake Time</td><td>60s</td><td>Resist Bake Time</td><td>90s</td></tr><tr><td>HMDS Amount (Drops)</td><td>2</td><td>Exposure Pattern</td><td>link</td></tr><tr><td>HMDS Spin Speed</td><td>4000 rpm</td><td>Exposure Source</td><td>Stepper V1</td></tr><tr><td>HMDS Spin Time</td><td>20s</td><td>Exposure Time</td><td>4s</td></tr><tr><td>HMDS Bake Temperature</td><td>100°C</td><td>Exposure Dose</td><td></td></tr><tr><td>HMDS Bake Time</td><td>60s</td><td>Developer Type</td><td>AZ-400K</td></tr><tr><td>Resist Amount</td><td>2 drops</td><td>Developer Time</td><td>80s</td></tr><tr><td>Resist Spin Speed</td><td>4000 rpm</td><td>Developer Temperature</td><td>20°C</td></tr><tr><td>Resist Spin Time</td><td>30s</td><td></td><td></td></tr></tbody></table>

#### For More Detailed Process Parameters:

[Patterning Process Sheet](https://docs.google.com/spreadsheets/d/1JrOyISOwiZrRkdBT3utiHOze-yCluFcrFgd6_dhLPMw/edit#gid=38181110)

***

## Purpose

Patterning is the core of any micro/nanofabrication process, as it is used to mask etch and deposit steps. First we spin coat photoresist to deposit a thin layer. Then we use our maskless lithography stepper to expose our pattern in the resist with light. Finally we wash away the exposed region with developer. This leaves behind a resist pattern that is resistant to many types of acid and plasma etches. It can also be hard baked and used as a dielectric, or metal can be deposited on top of it for a lift off process. The procedure described here uses a positive resist, AZ-P4210, but negative resists also exist where unexposed areas become soluble.

See the appendix for useful resources about spin coating, our resist, and developer.

***

## Tools

1. [Spin Coater](https://docs.google.com/document/d/16tg5COz3QADQcWTJfgbuTBRsJrYIF2IFitKL2VLnr3I/edit?usp=sharing)
2. [Hot Plate](https://docs.google.com/document/d/14IZRb_CLO6zwDDNvO9dSkzYD5jisfbr-6na2exCk-T0/edit?usp=sharing)
3. Flashlight Jig or Maskless Lithography Stepper

## Materials

1. [Hexamethyldisilazane (HMDS) adhesion promoter](https://docs.google.com/document/d/1Wtk8l1dXzwlhdUSQaCBSIJ00-sB0tanP0AOklIOY0Ik/edit?usp=sharing)
2. AZ-4210 positive photoresist ([specsheet](https://www.microchemicals.com/micro/tds_az_p4000_series.pdf))
3. AZ-400K Developer
4. Acetone
5. Isopropanol
6. Deionized water
7. Evaporating dish

***

## Procedure

### Preparation

1. If you have already claimed a chip number, and opened its specific chip view data sheet, record your patterning data into that sheet. If you have NOT claimed a chip number, and have NOT begun recording data in a chip specific sheet, open this [central chip count](https://docs.google.com/spreadsheets/d/1MrqtnkHcNr5hekHpQHusBZJG4nrdcxDz7Yg5Emn9BMQ/edit#gid=0) sheet, claim the next available chip number, open the blank chip view sheet for that specific chip number and record all subsequent process data into it.&#x20;
2. [Cleave](https://docs.google.com/document/d/1UWZ_X2TpRqdOWOC8YGubfD7xW-dz4nRNzJk5c_mo4w0/edit?usp=sharing) the Si wafer into a \~1 cm x 1 cm square.
3. Dust off the wafer with the nitrogen gun

### Wafer Cleaning

1. In the fume hood, hold the wafer with tweezers over the sink.
2. Rinse the polished side of the wafer thoroughly with acetone, then isopropyl alcohol.
   1. The acetone leaves a residue that must be removed by the isopropyl alcohol rinse.
3. Blow the wafer dry with the nitrogen gun.
   1. Even when the wafer appears dry, there may still be moisture on the edges, so dry liberally.
4. Inspect with the naked eye and note any marks on the wafer.
   1. Marks present after cleaning are likely scratches that need to be documented so we observe their effect on the process.

### Spin Coat

<figure><figcaption></figcaption></figure>

4. If previous steps required cleaning with solvents, pre-bake the wafer to dehydrate the surface.
5. If patterning on silicon, spin coat 1 drop of HMDS. Otherwise skip to 7.&#x20;
   1. Choose Time and RPM from [patterning data sheet](https://docs.google.com/spreadsheets/d/1T9-kXXxdD9c6KZh_iy1LGt8I8wGlmeVlIZmvBrkVQ2g/edit#gid=0)
6. Bake on the hot plate at 100°C for 30 seconds.
7. Spin coat as much photoresist as needed to mostly cover the chip, normally 2-3 drops
   1. Choose Time and RPM from [patterning data sheet](https://docs.google.com/spreadsheets/d/1T9-kXXxdD9c6KZh_iy1LGt8I8wGlmeVlIZmvBrkVQ2g/edit#gid=0)
   2.  If chip is having trouble sticking on o-ring either: try pressing top of chip while vacuum is on with some pressure to make a better seal (use plastic tweezers)

       
   3. Or, take o-ring off and clean then re-install.
8. Soft bake on the hot plate at 100°C for 90 seconds.

## Stepper Setup

1. Turn on the projector. Plug in the HDMI cable for the projector and the USB camera cable to your computer.
2. Plug in the Raspberry pi power adapter and press the button on the arduino nano to turn them on.
3. Set up the projector as a second screen on your computer’s  display settings.
4. Prepare patterns following [this guide](https://docs.google.com/document/d/1KSepVb3Hcj588Dh-XTc7v-McR3kzytuWSQJffmucU_Q)
5. Set up the patterning GUI util script
   1. Run the python script\
      It requires installing pillow and tkinter with pip3
   2. Move the black full-screen window to the projector (on windows, this is shift + win + L/R arrow)
   3. Use the three import buttons to select the desired images, these can be changed whenever. Make sure they are correct using the small previews
   4. Future mentions to GUI buttons will be in \[braces]
6. Put your image to be patterned in a Google Slides presentation. Example: [resolution tests](https://docs.google.com/presentation/d/16IsbOxES9O-imGjrv0Toe71-hkYhzWTv_O2MjYu2rck/edit?usp=sharing).&#x20;
   1. Put a black screen as the last slide in your presentation. This will be the non-exposing/”off” slide.
   2. Put another black screen as the second to last slide, this time adding a dark gray plus sign or other easily focusable feature. Ensure this feature is in an area that will either get exposed or isn’t used.

<br>

7. Copy the flat field correction mask from here and paste it on top of your pattern in google slides. Select the mask and go to format options > set opacity to 50%.
8. In your browser, navigate to [http://172.26.165.101:5000/#](http://172.26.165.101:5000). This is how you control the stage. Press “cancel” when it prompts you to calibrate.
9. Open AmScope.
10. Split the screen so you can see the browser with the stage control and AmScope at the same time.

### Expose Using Maskless Photolithography Stepper



1. Check that the red filter is inserted and the bandpass (UV) filter is out.
2. Place the chip with soft baked photoresist on the stage.
3. Press \[show red focus]&#x20;
4. Find your chip by moving it with tweezers, then rotate it so the pattern is the right way up.

<figure><figcaption><p>Example of focused view with red illuminuation</p></figcaption></figure>

16. Use the stage to rough focus and align. Use the arrow keys with the OpenFlexure control screen to move the stage. Use pg up/ pg down to move in Z. The plus sign grid pattern is useful for accurate focus.
17. Press \[clear] to project a black screen.
18. Move the Z stage by 1800 steps in +Z. This will switch from focusing in red to approximately focusing in UV.

<figure><figcaption><p>AmScope exposure and gain panel</p></figcaption></figure>

19. Turn the exposure time to 200-300ms and the gain all the way up on AmScope.
20. &#x20;Use an opaque, flat object to block the light coming out of the objective while you remove the red filter and insert the UV filter.

<figure><figcaption><p>UV focus marks.</p></figcaption></figure>

21. Press \[show UV focus] to show UV focusing pattern. Use the Z axis to focus. Try to do this as quickly as possible to avoid unnecessary exposure. Press \[clear] at any point to hide the focusing image.
22. &#x20;Set the desired patterning time (in milliseconds)
23. &#x20;Press the big red \[pattern] button when ready.
24. &#x20;Move on to your next pattern and repeat. If you’re aligning with an underlying pattern you need to switch back to red. Otherwise you can try stepping over and exposing in UV without refocusing.

## Develop

<figure><figcaption><p>Developer (Deionized water to AZ-400K 3:1) and DI water rinse.</p></figcaption></figure>

1. Refresh the developer if it has been out for more than 6 hours. Otherwise skip to step 3.
   1. Pour the used developer into the bottle labeled "developer waste"
   2. Rinse the evaporating dish with DI water.
   3. Pour about 30 mL of pre-diluted 3:1 AZ-400K developer solution into the evaporating dish labeled “AZ-400K 3:1”. For a sense of scale: in the dish above this should only be about 3mm tall of liquid (just enough to cover the surface of the chip)
   4. Fill another evaporating dish halfway with DI water.
2. Start the timer **at the same time as you drop the wafer into the developer**, photoresist side up.

<figure><figcaption><p>Agitate the developer</p></figcaption></figure>

5. Agitate the chip in the developer solution with quick, small circular motions. Watch [this video](https://drive.google.com/file/d/1C2APhZpUS7O2a-3hzmjMloyEuc7RCg1Z/view?usp=sharing) for proper technique.
6. 5 seconds before the end of the timer, pick up the chip and prepare to drop it into the water. The chip should **hit the water exactly at 0 seconds**.
   1. Note that development time includes all the time that developer is touching the chip, not just during agitation
7. Dry off the chip with compressed air.

## Inspect

1. Look at the chip with your bare eyes to help build an intuition for the process.
2. Put the chip under the microscope. Connect to the camera with your laptop and take pictures at 5X, 10X bright and dark field, 20X bright and dark field, and 50X.
   1. You can use the 10x or 20x objective and use the calibrated measuring system to determine feature sizes on your chip
3. Batch save then upload the folder to [Patterning Photos](https://drive.google.com/drive/folders/1-ON8-167CTyXiuhVdlI1_WMpKkx0M0a8?usp=share_link).
4. Paste a link to the folder in the last column of the patterning data sheet.
5. Put the chip away in a plastic box and label it with a serial number.

<figure><figcaption><p>Inspection image demonstrating non-uniform exposure</p></figcaption></figure>

Right side: thicker lines and blurry edges. Left side: thin lines and sharp edges.

<figure><figcaption><p>Inspection image showing blurring effect from defocused stepper</p></figcaption></figure>

<figure><figcaption><p>Insprction image showing incsufficient develop or exposure</p></figcaption></figure>

## Safety

1. HMDS is a toxic, volatile chemical that should only be used in the fume hood.
2. Photoresist, while not as bad as HMDS, contains some nasty solvents and should be cleaned with acetone if it gets on anything other than chips and the spin coater.
3. AZ-400K developer is a strong base containing KOH. Use the appropriate precautions for working with bases. Only agitate the developer inside the fume hood to reduce the chance of droplets.<br>

***

### Additional Resources

See this webpage for in depth spin coating theory: [https://www.ossila.com/en-us/pages/spin-coating](https://www.ossila.com/en-us/pages/spin-coating)

[AZ-P4210 techsheet](https://www.microchemicals.com/micro/tds_az_p4000_series.pdf)

[AZ 400K developer](https://www.microchemicals.com/micro/info_az_400k_421k_Developer.pdf)

### Alternative Exposure Technique: 365nm Flashlight

13. Put on UV protection glasses.
14. Before placing the chip under the exposure area, turn on the flashlight and adjust the position of the UV meter’s sensor head to maximize the reading.&#x20;
    1. Depending on the battery level, this should be around 10 mW/cm2.
15. Turn off the flashlight, being careful not to move it out of position.
16. Place the chip on the plastic cap photoresist side up.&#x20;
17. Place the mask on the wafer. Gently press down to sandwich the two together.
    1. If the ThorLabs logo is correctly oriented then the chrome is facing you. Put that side face down towards the chip.
    2. Try not to slide the mask on the wafer because you’ll damage the photoresist.
18. Place the cap with the wafer and mask on top of the UV sensor.
19. Turn on the flashlight for the desired exposure time.
20. &#x20;Record the measured exposure time in the [spreadsheet](https://docs.google.com/spreadsheets/d/1T9-kXXxdD9c6KZh_iy1LGt8I8wGlmeVlIZmvBrkVQ2g/edit?usp=sharing)
    1. Does should be automatically calculated in the sheet based on exposure option used

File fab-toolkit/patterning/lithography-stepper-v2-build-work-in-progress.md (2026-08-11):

---
icon: '2'
---

# Lithography Stepper V2 Build

**If you already have a stepper built and you're looking for information on how to operate the tool, check out our** [**SOP**](../../standard-operating-procedures/patterning-sop-stepper-v2/)**!**

## Hardware Specs

<table><thead><tr><th width="279">Cost</th><th>$3,015.44</th></tr></thead><tbody><tr><td>Approximate Build Time</td><td>6 hours</td></tr><tr><td>Optical Resolution</td><td>2 µm</td></tr><tr><td>Developed Resolution</td><td>2 µm</td></tr><tr><td>Tiling Alignment Accuracy</td><td>5 µm</td></tr><tr><td>Overlay Alignment Accuracy</td><td>5 µm</td></tr><tr><td>Reticle (Exposure) Dimensions </td><td>1.04mm by 0.58mm</td></tr><tr><td>Exposure Time</td><td>8 seconds</td></tr><tr><td>Mechanical Step Size</td><td>1.5 µm</td></tr><tr><td>Mechanical Repeatability</td><td>5 µm (to verify)</td></tr><tr><td>Maximum Wafer Size</td><td>2 cm by 2 cm</td></tr><tr><td>Tool Size</td><td>30 cm x 36 cm x 20 cm</td></tr></tbody></table>

## Hardware Description

Our design was based on [Sam Zeloof](http://sam.zeloof.xyz/maskless-photolithography/) and [Huygens Optics](https://www.youtube.com/watch?v=_w0Z2Y5vaAQ)’ versions of this tool, which is essentially a projector connected to a microscope. We use a 10x objective for demagnification and a mechanical XYZ stage for positioning.

Stepper version 2 has greatly improved optical and mechanical performance over V1 while using the same DLP chip from Texas Instruments. Several factors led to this improvement:

1. Instead of an off the shelf projector with a flimsy plastic housing, we switched to the [TI DLPDLCR471TPEVM evaluation board](https://www.ti.com/tool/DLPDLCR471TPEVM). This allows for a more robust physical connection to the projector housing, thus eliminating vibrations. It also has much better documentation.
2. By swapping to a finite conjugate microscope objective, the optical path length is reduced from \~250 to 160 mm. This reduces the moment of inertia of the optics subassembly, therefore also reducing vibration.
3. Swapping to LEDs instead of the broad spectrum mercury lamp removes the need to constantly swap filters, which introduced random perturbations from touching the optics. We replaced the stock blue LED with a 410 nm LED mounted on a custom PCB. The PCB design files can be found [here](https://drive.google.com/drive/u/1/folders/1DK4DBdWB0b6NKSaRz9XtcY19dkCHzusb).
4. Mounting the projector horizontally means less structure is needed.



## Tools Required

* M3 and M4 taps
* 3D printer
* Solder paste (preferably a syringe)
* Tweezers or pick and place machine
* Reflow oven
* Calipers

## Bill of Materials

Total Cost: $3,015.44 or\*\* $3106.44 (excluding computer & peripherals) (last updated March 16, 2025)

<table><thead><tr><th width="337">Name</th><th width="64">Qty</th><th width="128">Total</th><th>Link</th></tr></thead><tbody><tr><td>TI DLP Evaluation Module</td><td>1</td><td>$999</td><td><a href="https://www.ti.com/tool/DLPDLCR471TPEVM">TI</a></td></tr><tr><td>Assorted Optics</td><td>1</td><td>$736.52</td><td><a href="https://www.thorlabs.com/uploadcart/">Thorlabs</a>*</td></tr><tr><td>10X Din Plan Objective</td><td>1</td><td>$159</td><td><a href="https://www.edmundoptics.com/p/10x-din-plan-commercial-grade-objective/5386/">Edmunds</a></td></tr><tr><td>Basler acA1920-40uc w/ Sony IMX249 <br>(recommended), or**<br>FLIR Blackfly S Camera w/ Sony IMX183</td><td>1</td><td>$609.00<br>or**<br>$700.00</td><td><a href="https://www.baslerweb.com/en-us/shop/aca1920-40uc/">Basler</a><br>or**<br><a href="https://www.edmundoptics.com/p/bfs-u3-200s6c-c-usb3-blackflyreg-s-color-camera/40178/">Edmunds</a></td></tr><tr><td>USB Type A to Micro B locking cable</td><td>1</td><td>$25</td><td><a href="https://www.edmundoptics.com/p/usb-30-locking-cable-3m-length/29172/">Edmunds</a></td></tr><tr><td>19V 4.74A Projector Power Supply</td><td>1</td><td>$17.99</td><td><a href="https://www.amazon.com/Nobsound-Adapter-Universal-Charger-100-240V/dp/B074J81XRB/ref=sr_1_9?keywords=19v+power+supply&#x26;qid=1685981984&#x26;sr=8-9">Amazon</a></td></tr><tr><td>XYZ Stage 40mm</td><td>1</td><td>$125</td><td><a href="https://www.amazon.com/Pricision-40x40mm-Trimming-Bearing-Platform/dp/B07D7N9GT6/ref=sr_1_4?crid=32WSW494CE1YE&#x26;keywords=30mm+xyz+stage&#x26;qid=1706559232&#x26;sprefix=30mm+xyz+stage%2Caps%2C80&#x26;sr=8-4&#x26;ufe=app_do%3Aamzn1.fos.f5122f16-c3e8-4386-bf32-63e904010ad0">Amazon</a></td></tr><tr><td>Rotation Stage</td><td>1</td><td>$69.34</td><td><a href="https://www.amazon.com/Displacement-Platform-FineTuning-Production-Machinery/dp/B0972XB4NW/ref=sr_1_3?crid=2M0YGWAA27LQA&#x26;keywords=60mm+rotation+stage&#x26;qid=1706559352&#x26;sprefix=60mm+rotation+stage%2Caps%2C112&#x26;sr=8-3">Amazon</a></td></tr><tr><td>NEMA 28 Steppers</td><td>4</td><td>$71.96</td><td><a href="https://www.amazon.com/gp/product/B07PNV7RBW/ref=ox_sc_act_title_1?smid=A3HCJ70Z0RHBT6&#x26;th=1">Amazon</a></td></tr><tr><td>Arduino Uno (Elegoo)</td><td>1</td><td>$16.99</td><td><a href="https://www.amazon.com/ELEGOO-Board-ATmega328P-ATMEGA16U2-Compliant/dp/B01EWOE0UU/ref=sr_1_6?crid=25HW74RSV1WUQ&#x26;keywords=arduino&#x26;qid=1706561234&#x26;sprefix=arduino%2Caps%2C115&#x26;sr=8-6">Amazon</a></td></tr><tr><td>CNC Shield for Arduino V3.0</td><td>1</td><td>$9.99</td><td><a href="https://www.amazon.com/Organizer-Expansion-Stepper-Heatsink-Arduino/dp/B07TT3C3HB/ref=sr_1_1?crid=3U63T1GH2IYGH&#x26;keywords=arduino+stepper+shield&#x26;qid=1706561169&#x26;sprefix=arduino+stepper+shield%2Caps%2C104&#x26;sr=8-1">Amazon</a></td></tr><tr><td>Stepper Motor Drivers</td><td>1</td><td>$22.99</td><td><a href="https://www.amazon.com/BIGTREETECH-Direct-TMC2208-TMC2209-TMC5160/dp/B07ZPYKL46?th=1">Amazon</a></td></tr><tr><td>Shield Power Supply 12V</td><td>2</td><td>$23.98</td><td><a href="https://www.amazon.com/ALITOVE-Adapter-Converter-100-240V-5-5x2-1mm/dp/B01GEA8PQA/ref=sr_1_4?keywords=12v+power+supply&#x26;qid=1706561572&#x26;sr=8-4">Amazon</a></td></tr><tr><td>2.5mm Barrel Connector</td><td>1</td><td>$7.99</td><td><a href="https://www.amazon.com/Fancasee-Replacement-Degree-Pigtail-Supply/dp/B081TXY6ML/ref=sr_1_3?crid=1LPRM16V3EL0T&#x26;keywords=2.5mm+dc+plug+pigtail&#x26;qid=1706561706&#x26;sprefix=2.5mm+dc+plug+pigtail%2Caps%2C94&#x26;sr=8-3">Amazon</a></td></tr><tr><td>Vacuum pump for chuck</td><td>1</td><td>$26.52</td><td><a href="https://www.amazon.com/Vacuum-diaphragm-compressor-75KPA-vacuum/dp/B08RCRJH9M">Amazon</a></td></tr><tr><td>M2.5 Screw Assortment</td><td>1</td><td>$30.56</td><td><a href="https://www.amazon.com/VIGRUE-Button-Washers-Assortment-Storage/dp/B08VHVB4H5/ref=sr_1_3?crid=24MVS2UJSXWC&#x26;keywords=m2.5&#x26;qid=1695828225&#x26;sprefix=m2.5%2Caps%2C112&#x26;sr=8-3">Amazon</a></td></tr><tr><td>Collapsible Magnetic Tray for Vibration</td><td>1</td><td>$21.99</td><td><a href="https://www.amazon.com/Collapsible-Magnetic-Foldable-Silicone-Organizes/dp/B0B7JBHK2N">Amazon</a></td></tr><tr><td>410nm Lumiled LED</td><td>4</td><td>$40.20</td><td><a href="https://www.digikey.com/en/products/detail/lumileds/L1F3-U400200012000/7389568">Digikey</a></td></tr><tr><td>Pico-spox 10pos Vertical Connector</td><td>2</td><td>$1.42</td><td><a href="https://www.digikey.com/en/products/detail/molex/0874371043/717647">Digikey</a></td></tr></tbody></table>

\*Upload this CSV file to Thorlabs for all the optomechanical parts + beamsplitter.

{% file src="../../.gitbook/assets/StepperV2_Thorlabs_BOM.csv" %}

\*\*The Basler camera and FLIR camera are mechanically interchangeable, but our software implementation for the Basler camera is more reliable and freely accessible (FLIR code distribution is restricted). For software installation simplicity, we recommend using the Basler camera.

## Design File Summary

Note: the OnShape folder is organized poorly because it was our first time using it. Won't happen again, we promise!

<table><thead><tr><th width="216">File Name w/ link</th><th width="315">Description</th><th width="69">QTY</th><th>Tools Used</th></tr></thead><tbody><tr><td><a href="https://cad.onshape.com/documents/64016e74334e9df7f3829a37/w/da5b11336b83f611c84f6d9f/e/345550da08271685cbf13c97">Stepper V2 Assembly</a></td><td>Reference for assembling optical components</td><td>1</td><td>Driver kit</td></tr><tr><td><a href="https://cad.onshape.com/documents/64016e74334e9df7f3829a37/v/b7cf6897006e1bbfe46b354b/e/0e8c1f104c4c4708545e72bb">Adapter plate</a></td><td>Connects the optics to the projector. Matches hole pattern on DLP housing and <a href="https://www.thorlabs.com/thorproduct.cfm?partnumber=SM1A53">Thorlabs flange</a>.</td><td>1</td><td>Water jet/<br>Online CNC shop/<br>3D print</td></tr><tr><td><a href="https://cad.onshape.com/documents/052936cc5219e79ce8b1d191/w/decf2990870bd6e2bca78fa2/e/bd3bd601a477f0977cdc93cc">Base Plate</a></td><td>Structural base for aligning the micropositioning stage to the projector and optics.</td><td>1</td><td>Manual mill/<br>Online CNC shop/<br>Water jet</td></tr><tr><td><a href="https://cad.onshape.com/documents/7046af5f6b7e48bd4bd933bb/w/60cbad214f94f1caf8b51a12/e/e2e1e76eaab599d9a1c4501e">40mm Stepper Mount</a> (link to <a href="https://drive.google.com/drive/u/1/folders/179fKzkOVRPVE_OXGE6WHWXImXfUCj_XX">SW</a>)</td><td>Three parts that connect stepper motors to the micropositioning stage x , y and z axes.</td><td>1</td><td>3D printed</td></tr><tr><td><a href="https://cad.onshape.com/documents/3f7d616dea69d10f46394ab8/w/89eaec6dabe956215608e0d5/e/7d51357363ef098a886662ee">Sliding Shaft Coupler</a></td><td>Press fits onto micrometer and slides on motor D-shaft.</td><td>3</td><td>3D printed</td></tr><tr><td><a href="https://cad.onshape.com/documents/7046af5f6b7e48bd4bd933bb/w/60cbad214f94f1caf8b51a12/e/fa5e024aa8cfe72d30af884d">Spacer</a></td><td>Tiny part for offsetting micrometer stop on Y axis</td><td>1</td><td>3D printed</td></tr><tr><td><a href="https://cad.onshape.com/documents/64016e74334e9df7f3829a37/w/da5b11336b83f611c84f6d9f/e/ffd5f395bec2204af40685e2">60mm Theta to 40mm XYZ Bracket</a></td><td>Mounts the theta stage at a right angle to the rest of the stage.</td><td>1</td><td>3D printed</td></tr><tr><td><a href="https://cad.onshape.com/documents/f6235112d9655ce90371982d/w/a0efdc80157be57df12af66d/e/fe48a0682c07d2cebc332aac">Vacuum Chuck</a></td><td>Connects to a vacuum hose to hold the chip. Corner jig aids alignment.</td><td>1</td><td>3D printed</td></tr><tr><td><a href="https://github.com/hacker-fab/stepper">Stepper Software</a></td><td>Python script for controlling the projector. Check for recent version.</td><td></td><td>Laptop</td></tr><tr><td><a href="https://github.com/gnea/grbl">GRBL Arduino CNC firmware</a></td><td>Firmware for stage microcontroller.</td><td></td><td>Arduino Uno, IDE, Laptop</td></tr></tbody></table>

## Build Instructions

Building the Stepper V2 requires some simple CNC machining, PCB soldering, 3D printing, and other assembly steps, followed by software installation.

### Get the Metal Parts Made

<figure><figcaption><p>Base Plate</p></figcaption></figure>

<figure><figcaption><p>Adapter Plate</p></figcaption></figure>

There are several options for fabricating these two parts: the Base Plate and Adapter Plate. If you have access to a water jet, you may cut these parts from 1/4" aluminum plate, available on [McMaster](https://www.mcmaster.com/8975K437-8975K846/). Otherwise you can order the parts from [SendCutSend](https://sendcutsend.com/services/waterjet-cutting/), [Xometry ](https://www.xometry.com/capabilities/sheet-cutting/waterjet-cutting/)or another online CNC shop.

#### Option 1: Water Jet

The Base Plate is 15" long, so double check that your water jet is large enough.

When downloading the Adapter Plate DXF for water jetting, go to Config > Water jet to get the hole sizes right for tapping. The 2.2mm holes are clearance for M2, and the 2.5mm holes are M3 tapped and countersunk.

#### Option 2: CNC Shop

[Click here for a SendCutSend](https://cart.sendcutsend.com/c2ynz1un076a) shopping cart with the parts already uploaded and configured. This has not been tested yet.

#### Option 3: Manual Machining

Base Plate: [Click here](https://cad.onshape.com/documents/052936cc5219e79ce8b1d191/w/decf2990870bd6e2bca78fa2/e/bd3bd601a477f0977cdc93cc) for a drawing to have open while drilling all the holes. Start with a center drill then use an appropriately sized drill bit for M4 and M6 holes. You may also switch to 8-32 and 1/4-20 if you already have the taps for those, and no other parts will change if you do so.

Adapter plate: This should be manually machinable but we haven't tried.

### Solder the UV LED PCB

The PCB Gerber files for our UV LED can be found [here](https://drive.google.com/drive/u/1/folders/1X3nmuruO58prPQBm8DrWUhfM-LNq0qWm). We provide a screenshot of the layout in Altium and a 3D render of the PCB below.





You can order it through your PCB manufacturer of choice (we used JLCPCB). However, note that the PCB is [**copper core**](https://jlcpcb.com/blog/62-JLCPCB-Direct-Heatsink-Copper-Cored-PCBs-Available-Now!). This is because the LEDs draw several amps of current in operation. To ensure that the PCB doesn't melt, you should use copper core to facilitate better heat flow.\
\
When ordering the PCB, the manufacturer might send you an email asking about a missing heatsink file. In this case, please respond that this project does not include a direct heatsink, as the copper core PCB itself is designed to handle the thermal management.

We used 410 nm UV LEDs on this PCB. We found that two LEDs in series is sufficient to produce enough UV light for patterning. We also found connectors that are compatible with the cable in the TI DLP dev kit.

When assembling the UV LED PCB, it is easiest to use a solder syringe to carefully deposit the paste onto the LED pads and connector pads. If you try to use a stencil mask, it is very easy to smear the paste, so this is not recommended.&#x20;

Once the paste is applied, align the components with their pads (i.e. using tweezers or a pick and place machine). Keep in mind that you need to use a nozzle that is small enough to pick up the LEDs. Finally, you can put the PCB into a reflow oven to solder the components to the board.

Below is a completed version of the PCB - **note the polarity!** This image shows the correct orientation of the LEDs (credit to University of Utah for the photo). If you have it flipped, then the projector will project an image briefly before shutting itself off:\


You can test by applying 6V (limit to 1A) across the LED leads, but **be sure to wear UV-protective glasses**, as the LEDs will be bright! Once you are confident that the PCB works, you can now replace the blue LED PCB in the TI DLP dev kit with our new UV LED PCB. To see the UV light, simply look at the leds through your phone's camera, as the sensors see it as purple light.

### Disassemble the TI DLP dev kit

Taking pictures after every step is key to ensuring you can put it back together properly.

<figure><figcaption><p>it works!</p></figcaption></figure>

1. Test the projector before we completely take it apart :)

<figure><figcaption><p>LED current settings in the software</p></figcaption></figure>

2. Plug in the projector over USB and use the [LightCrafter GUI software](https://www.ti.com/tool/download/DLPDLC-GUI) to set the LED current drive level to 150. Note 150 is NOT the output current, that can be calculated like so: `OutputCurrent = ((DriveLevel + 1)/1024)*((0.15/0.036))`  - [Table 19-91](https://www.ti.com/lit/ug/dlpu110b/dlpu110b.pdf) . (The projector defaults to 1023 ⇒ 4A, which is its maximum output - our UV LEDs are not able to handle that much current, so reducing the current makes sure they don't burn out!)

<figure><figcaption></figcaption></figure>

3. Unplug all the connectors and remove the top PCB by unscrewing the standoffs.

<figure><figcaption></figcaption></figure>

4. Remove the side PCB.

<figure><figcaption></figcaption></figure>

5. Unscrew and remove the shroud by sliding it away from the rest of the optics.

<figure><figcaption></figcaption></figure>

6. Unscrew and remove the heatsink for the front-most LED, which should be the blue one.

t

7. Disconnect the LED PCB from the cable. Heat it slightly on a hot plate or with a hot air gun to soften the adhesive and remove the black plastic housing.
8. Glue the black plastic piece to the DIY UV LED PCB, connect it to the blue cable, and reattach it to the optics housing. Put the heatsink back as well.

<figure><figcaption></figcaption></figure>

9. Unscrew the projection lens. That one makes things bigger, but we're trying to make things smaller. It's got to go.

<figure><figcaption></figcaption></figure>

10. Screw on the adapter plate with four countersunk M2 screws.

<figure><figcaption></figcaption></figure>

11. Reassemble the rest of the projector, including the shroud and the PCBs.

### Assemble the Optics

See [CAD](https://cad.onshape.com/documents/64016e74334e9df7f3829a37/w/da5b11336b83f611c84f6d9f/e/345550da08271685cbf13c97) for interactive assembly help (select option 3)

<figure><figcaption><p>All the tubes!</p></figcaption></figure>

<figure><figcaption></figcaption></figure>

1. Start with the beamsplitter cube. Unscrew the set screws, remove the holder, and clip in the beamsplitter. The text ("Thorlabs") should be facing the microscope objective and camera when the holder is reinserted. Keep track of this during assembly and fix it later if necessary.

<figure><figcaption></figcaption></figure>

<figure><figcaption></figcaption></figure>

2. Assemble the DLP tube. From left to right, the parts in the first picture are 0.3" lens tube (SM1L03), 0.5" lens tube coupler (SM1CPL05), 0.5" adjustable lens tube (SM1V05), and 0.5" lens tube (SM1L05). You may want to remove any internal lens rings. The adjustable lens tube allows axial length adjustment and the coupler allows rotation about the optical axis.

<figure><figcaption></figcaption></figure>

3. Screw the DLP tube into the beamsplitter cube. The correct orientation is shown above, and the arrow points to the side of the beamsplitter with the text (and optical coating).
4. Assemble the camera tube, which similarly constructed. The parts are 1" lens tube (SM1L10), 1" lens tube coupler (SM1CPL10), 1" adjustable lens tube (SM1V10), another 1" lens tube (SM1L10), and C-mount SM1 adapter (SM1A9) (last two shown below).

<figure><figcaption></figcaption></figure>

5. Make sure this camera tube is 82.3 mm long. We calculate this number by subtracting the various component lengths from the standard microscope objective back focal length of 160mm: 160 - 17.5 (c-mount camera) - 22.1 (objective tube) - 38.1 (beamsplitter cube).\
   \
   **(NOTE:** The calculation here is done incorrectly, but we have successfully been using it without major issues. The correct back focal length is 150mm, see [this page](https://www.edmundoptics.com/knowledge-center/application-notes/microscopy/understanding-microscopes-and-objectives/) and the diagram below)

<figure><figcaption><p>Camera and beamsplitter cube should be parallel.</p></figcaption></figure>

{% columns %}
{% column width="50%" %}
<figure><figcaption><p>Optical Path Length Diagram Annotated from CMU's <a href="https://cad.onshape.com/documents/64016e74334e9df7f3829a37/w/da5b11336b83f611c84f6d9f/e/345550da08271685cbf13c97">CAD </a>(Contributed by UIUC)</p></figcaption></figure>
{% endcolumn %}

{% column width="50%" %}
<figure><figcaption><p>Objective Tube Calculations for 150mm focal length (useful in case using non-exact parts lengths)</p></figcaption></figure>
{% endcolumn %}
{% endcolumns %}

6. Screw on the C-mount SM1 adapter (SM1A9) to the camera and the 1" lens tube. Adjust the lens tube coupler to align the camera with the beamsplitter cube.

<figure><figcaption></figcaption></figure>

7. Assemble the objective tube, which consists of a 0.5" lens tube (SM1L05), a 0.3" lens tube (SM1L03) an SM1 to RMS adapter (SM1A3), and the microscope objective.

<figure><figcaption></figcaption></figure>

8. Temporarily loosen the top lens tube coupler in order to finally screw the entire assembly into the projector.

### 3D Print and Assemble the Stage

Print all of the parts in the table below. Black PLA is fine. You may need to re-orient them so they print well. The stepper mounts will all need small supports in the motor flange. The X and Y axes need other supports as well.

<table><thead><tr><th width="315">File Name w/ link</th><th width="362">Description</th><th width="224">QTY</th></tr></thead><tbody><tr><td><a href="https://cad.onshape.com/documents/7046af5f6b7e48bd4bd933bb/w/60cbad214f94f1caf8b51a12/e/e2e1e76eaab599d9a1c4501e">40mm Stepper Mount</a> (link to <a href="https://drive.google.com/drive/u/1/folders/179fKzkOVRPVE_OXGE6WHWXImXfUCj_XX">SW</a>)</td><td>Three parts that connect stepper motors to the micropositioning stage x , y and z axes.</td><td>1</td></tr><tr><td><a href="https://cad.onshape.com/documents/3f7d616dea69d10f46394ab8/w/89eaec6dabe956215608e0d5/e/7d51357363ef098a886662ee">Sliding Shaft Coupler</a></td><td>Press fits onto micrometer and slides on motor D-shaft.</td><td>3</td></tr><tr><td><a href="https://cad.onshape.com/documents/7046af5f6b7e48bd4bd933bb/w/60cbad214f94f1caf8b51a12/e/fa5e024aa8cfe72d30af884d">Spacer</a></td><td>Tiny part for offsetting micrometer stop on Y axis</td><td>1</td></tr><tr><td><a href="https://cad.onshape.com/documents/64016e74334e9df7f3829a37/w/da5b11336b83f611c84f6d9f/e/ffd5f395bec2204af40685e2">60mm Theta to 40mm XYZ Bracket</a></td><td>Mounts the theta stage at a right angle to the rest of the stage.</td><td>1</td></tr><tr><td><a href="https://cad.onshape.com/documents/f6235112d9655ce90371982d/w/a0efdc80157be57df12af66d/e/fe48a0682c07d2cebc332aac">Vacuum Chuck</a></td><td>Connects to a vacuum hose to hold the chip. Corner jig aids alignment.</td><td>1</td></tr></tbody></table>

1. Unscrew all the, micrometers, L-stops and stage locks from the micrometer stage. Separate the X, Y and Z axes. Throughout the assembly process we will be replacing the stock screws with \~4mm longer ones as we reattach the various components to the stage. All 3d printed mounts are 4mm thick at the screw holes. Have your M2.5 screw kit handy!

<figure><figcaption></figcaption></figure>

2. Press fit the three sliding shaft couplers onto the three micrometer handles until the knurled surface is fully covered. They should fit with significant force and maybe gentle hammering. Be careful - the micrometer handles may have different diameters so you may need to modify the CAD and reprint to get a correct fit.

<figure><figcaption></figcaption></figure>

3. The shaft couplers should slide on the motor shafts with zero slop. Modify dimensions and re-print if this is not the case. Graphite lubricant may help decrease sliding friction, and the fit will get looser after repeated axial movement as the steel deforms and smooths the plastic.

<figure><figcaption></figcaption></figure>

4. Screw the motor, coupler, and micrometer into the X axis motor mount as shown. Doing this step before attaching to the rest of the stage takes advantage of the slop in the micrometer mounting screws and aids alignment.

<figure><figcaption></figcaption></figure>

<figure><figcaption></figcaption></figure>

5. Slide the Y axis motor mount onto the Y axis. You will need to remove some screws and push the stage to allow it to slide on.

<figure><figcaption></figcaption></figure>

6. Attach the motor. Don't screw down the micrometer mount yet.

<figure><figcaption></figcaption></figure>

7. While pushing the stage so the micrometer isn't touching the stop, fasten the micrometer mount. This avoids preloading the micrometer/motor assembly and improves shaft alignment.

<figure><figcaption></figcaption></figure>

7. Reattach the X axis micrometer stop as well. You may need to adjust the screw length to get it to fit.

<figure><figcaption></figcaption></figure>

<figure><figcaption></figcaption></figure>

<figure><figcaption></figcaption></figure>

8. Insert the Z axis motor mount to the Z axis. The easiest way to do this is to insert it upside down from the opposite side, then flip it while pushing the stage up, then slide it back so the holes line up. Basically it takes some fiddling.

<figure><figcaption></figcaption></figure>

9. As with the other stages, attach the motor first, then secure the mounts. Tighten the set screw at the green arrow. Make sure the micrometer is flush with the mount at the yellow arrow. Again pushing upwards at the red arrow eliminates prelaod from the spring inside the stage and helps alignment.

<figure><figcaption></figcaption></figure>

10. Tighten down the Z axis mount.

<figure><figcaption></figcaption></figure>

11. Attach the X axis motor mount to the stage with the screws at the red arrows.

<figure><figcaption></figcaption></figure>

12. Add additional screws on the X and Y axes to make sure the mounts are solidly attached. Ignore the spring in the above image.

<figure><figcaption></figcaption></figure>
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

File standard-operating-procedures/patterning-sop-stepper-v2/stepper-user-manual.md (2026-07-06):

---
description: >-
  A User Manual for the stepper software GUI application. Note that this
  document is a work in progress and is subject to changes frequently based on
  what updates and improvements are being made.
icon: readme
---

# Stepper User Manual

## Startup

Ensure that you've assembled the stepper and connected all ports and cables to their respective locations AND cloned the stepper repository and downloaded the necessary modules specified in the stepper repository's README file before proceeding to try out the GUI application.&#x20;

<figure><figcaption><p>Source: <a href="https://www.eizoglobal.com/library/basics/windows-10-multi-display-function/index.html">https://www.eizoglobal.com/library/basics/windows-10-multi-display-function/index.html</a></p></figcaption></figure>

To start the software in the manual in the terminal, type in the following commands. Alternatively, you may also create a bash script that does the same below

```
cd stepper/
uv run src/gui.py
```

Next, a window will pop up, in which you'll select the configuration file you wish to use to setup the stepper settings. You may reference the `default.toml` file in the stepper repository to customize your stepper configuration, then select that file and let the stepper software continue to run.&#x20;

**\[Optional]** When your configuration file enables homing, the stepper stage will startup by homing all axes. The ideal motion would be for the x and y stage to home _towards_ the proximity sensors in parallel, then the z-stage homes afterwards.&#x20;

After a few seconds, the GUI software will show up, and a window prompt will appear to request that the user switch the display. On a Windows Desktop/Laptop, the command to proceed with is `Win + Shift + Left` or `Win + Shift + Right` depending on which display frame shows the GUI and which shows the projection. _Ensure that your display settings are configured such that they are in "Extend display" mode._&#x20;

<figure><figcaption></figcaption></figure>

Now, you've officially completed all the setup stages to using the software. To see the camera display in "Safe Mode," you may click on the "Red Mode" tab to enter the mode ready for placement of chips containing spin-on photoresist onto the chip platform.&#x20;

<figure><figcaption></figcaption></figure>
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

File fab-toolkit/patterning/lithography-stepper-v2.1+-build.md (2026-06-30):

---
icon: arrow-up-right-dots
---

# Lithography Stepper V2.1+ Build

Stepper V2.1 is an incremental improvement upon the existing [Stepper V2](lithography-stepper-v2-build-work-in-progress.md) with mechanical improvements. As such, a lot of the content here will be the same as V2! The changes from V2 (and reasoning):

* Rotate the optics so that the objective points downward instead of sideways
  * This allows using the much-improved X and Y axes of the stage, instead of X and Z, which permits higher movement resolution and repeatability
  * This also means that we no longer need the vacuum chuck, which means reduced vibration (and less complexity)
  * Unlike Stepper V1, which was cantilevered, V2.1 is supported on all sides by rigid optical mounting posts, which should avoid V1's vibration issues
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

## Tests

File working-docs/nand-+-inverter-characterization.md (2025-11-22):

# NAND + Inverter Characterization

Fabrication and Testing of Enhancement Load NMOS Inverter Based on HackFab’s Standard  Process Flow

1. Introduction

NOT gate or inverter outputs the opposite of its input as shown in Table 1 is a basic but crucial part of the digital logic circuit. An NMOS logic inverter normally consists of two parts, a resistive load connected between the supply voltage (VDD) and the output as the “pull up” part and a switching transistor as the “pull down” part. To save device area and fabrication cost, instead of using resistors for the load, an active load such as an enhancement load transistor is used in the design as shown in Figure 1 (left). Enhancement load means a transistor’s gate and the drain are both connected to the supply voltage and make the transistor always in the saturation region. However, this causes there will be a constant current going through the transistors even if it is not performing which makes NMOS logic technology have higher power consumption and eventually be replaced by CMOS technology.

| Input | Output |
| ----- | ------ |
| 0     | 1      |
| 1     | 0      |

Table 1. Inverter Truthtable

<br>

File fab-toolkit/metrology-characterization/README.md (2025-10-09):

# 🔍 Metrology / Characterization

<table data-view="cards"><thead><tr><th></th><th data-type="content-ref"></th></tr></thead><tbody><tr><td>Probe Station</td><td><a href="semiconductor-parameter-analyzer/probe-station.md">probe-station.md</a></td></tr><tr><td>SMU</td><td><a href="semiconductor-parameter-analyzer/">semiconductor-parameter-analyzer</a></td></tr><tr><td>CV Measurements Guide</td><td><a href="cv-measurements.md">cv-measurements.md</a></td></tr><tr><td>IC Packaging</td><td><a href="ic-packaging.md">ic-packaging.md</a></td></tr></tbody></table>

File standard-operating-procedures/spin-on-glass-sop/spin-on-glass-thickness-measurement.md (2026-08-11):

---
description: >-
  *This only works with SoG on pure silicon and NOT polysilicon. Should work for
  both 700B/P5O4
---

# Spin on Glass Thickness Measurement

## **Purpose**&#x20;

The main purpose of this SOP is to describe a method that we can use to approximate the thickness of SoG. This is especially important in certain plasma etching processes, where removal of SiO2 is needed.

## **Tools**

* Spectrometer&#x20;
* Spectrogryph opened on computer connected to microscope view&#x20;
* [Calibration Graphs ](https://drive.google.com/file/d/1EVPOQWZP0WPVBpyYRbd6CC1ia3PgCf_a/view?usp=drive_link)(should end with .sgd, can only be opened in the Spectrogryph app)

Picture of Spectrometer Below:



## **Materials**

* Silicon Chip with 700B/P5O4 SOG

## Steps&#x20;

## _**Setting up the software + obtaining spectrometer data**_

First, ensure that the spectrometer is connected to the computer.&#x20;

In addition, place SoG on silicon chip sample on the slide under the microscope.

1. Open Spectrogryph software on Computer&#x20;
2. Under Plot/Views, select “New Acquisition View”



After which, you should see something that looks like:

<figure><figcaption><p>New Acquistion View</p></figcaption></figure>

3. In the upper left corner, select “Device Type” and select ASEQ. Then press connect.
4. Change exposure to 5000 ms (or more, if you want less noisy data)
5. Select single shot or continuous&#x20;
   1. Use Single Shot if you want to get one graph that is taken after 5 seconds of exposure
   2. Use Continuous if you want a graph that is constantly being recorded (hence changing)
6. Pressing “Acquire” would start the readings. Before pressing “Acquire”, ensure that the probe is connected to the microscope (will need to press the probe against the microscope to get good readings, as shown in picture below).



\
7\. Once a graph of Count against Wavelength is obtained,  we need to normalise the counts. This is done by clicking on "Process" and "Normalise (Peak)".

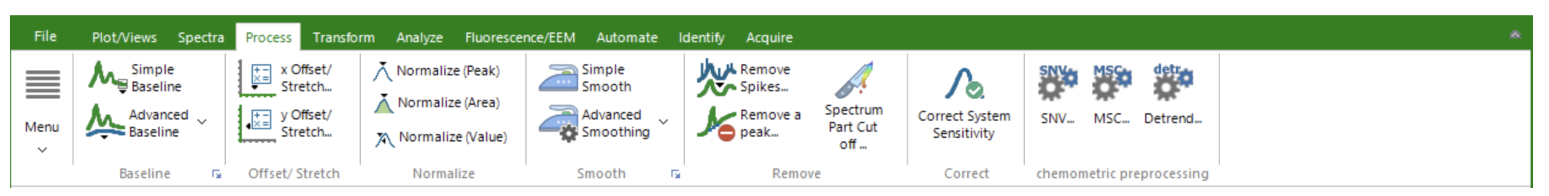
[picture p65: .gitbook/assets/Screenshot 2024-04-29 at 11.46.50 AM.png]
<figure><figcaption></figcaption></figure>

8. Once normalized, we can now save this spectral plot in file (save it in the .sgd format, so that you can re-open it in spectrogryph later)&#x20;

\
_**Determining Thickness of SoG**_

9. Create another New Acquisition View
10. Drag the [Calibration graphs file](https://drive.google.com/file/d/1EVPOQWZP0WPVBpyYRbd6CC1ia3PgCf_a/view) (should end with .sgd) into the New Acquisition View

You should see this:

<figure><figcaption><p>Calibration Graphs</p></figcaption></figure>

The color of the graphs correspond to the actual observed colors of the glass. This can serve as a good benchmark as to what the thickness of your glass might be.

As seen, the SoG with the lowest thickness (190 nm) had the maximum peak at a wavelength of \~590nm. As the glass thickness increases from 190 nm to 255 nm, the wavelength at maximum peak increased accordingly. Following that, from 255 nm to 276 nm, it can be seen that a second peak is starting to form (at a wavelength of around 480 nm). Finally, from 276 nm to 314 nm, the peak at 590 nm disappears, and now the peak at 480 nm becomes more distinct.&#x20;

11. Lastly, drag the .sgd file that you previously saved in Step 7 into the plot above.
12. Determine which shape your graph most closely resembles to determine SoG thickness.

**Also note that the color of your glass is a pretty good indicator of what thickness it will be.** So for instance, if your chip looks pink, just by looking at the calibration graphs, we can determine that thickness is around 270 nm.

## Useful Links

* Spectrogryph Manual Website: [https://www.effemm2.de/spectragryph/about\_help\_manual.html](https://www.effemm2.de/spectragryph/about_help_manual.html)
*

<br>

## &#x20;        <br>

\
\
\
\
\
\
\
\
\
\
\
\
\
\
\
\
\
<br>

<br>

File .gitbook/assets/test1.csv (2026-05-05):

host_time_s | device_millis | vswr | forward_v | reverse_v | motor1_pos_rad | motor2_pos_rad | at_match
1777485249.02027 | 11094 | -2.331922 | nan | nan | nan | nan | 1
1777485249.93498 | 12009 | -2.311836 | nan | nan | nan | nan | 1
1777485250.29177 | 12367 | -2.703165 | nan | nan | nan | nan | 1
1777485250.91806 | 12992 | -2.519638 | nan | nan | nan | nan | 1
1777485251.90125 | 13976 | -2.771296 | nan | nan | nan | nan | 1
1777485253.85526 | 15929 | -4.589738 | nan | nan | nan | nan | 1
1777485254.22498 | 16299 | -2.503521 | nan | nan | nan | nan | 1
1777485255.17448 | 17248 | -2.348943 | nan | nan | nan | nan | 1
1777485255.66805 | 17742 | -2.1267 | nan | nan | nan | nan | 1
1777485256.20831 | 18282 | -2.301106 | nan | nan | nan | nan | 1
1777485257.27659 | 19351 | -2.615028 | nan | nan | nan | nan | 1
1777485257.56608 | 19640 | -2.206614 | nan | nan | nan | nan | 1
1777485257.78689 | 19861 | -4.999994 | nan | nan | nan | nan | 1
1777485258.04253 | 20116 | -5.647048 | nan | nan | nan | nan | 1
1777485258.40826 | 20482 | -2.320352 | nan | nan | nan | nan | 1
1777485259.4591 | 21534 | -2.467855 | nan | nan | nan | nan | 1
1777485259.68025 | 21755 | -2.478459 | nan | nan | nan | nan | 1
1777485259.7652 | 21840 | -2.409484 | nan | nan | nan | nan | 1
1777485260.00372 | 22078 | -3.695036 | nan | nan | nan | nan | 1
1777485260.56173 | 22636 | -2.280994 | nan | nan | nan | nan | 1
1777485260.78277 | 22857 | -2.412031 | nan | nan | nan | nan | 1
1777485261.40882 | 23483 | -2.431242 | nan | nan | nan | nan | 1
1777485262.00458 | 24078 | -4.372276 | nan | nan | nan | nan | 1
1777485263.08935 | 25164 | -3.225351 | nan | nan | nan | nan | 1
1777485263.37545 | 25450 | -2.616313 | nan | nan | nan | nan | 1
1777485263.83471 | 25909 | -2.500003 | nan | nan | nan | nan | 1
1777485264.00641 | 26079 | -4.737961 | nan | nan | nan | nan | 1
1777485264.12704 | 26198 | -10.565201 | nan | nan | nan | nan | 1
1777485264.23258 | 26307 | -2.115242 | nan | nan | nan | nan | 1
1777485264.34121 | 26416 | -2.343355 | nan | nan | nan | nan | 1
1777485264.85208 | 26926 | -2.24051 | nan | nan | nan | nan | 1
1777485265.15846 | 27233 | -192.995834 | nan | nan | nan | nan | 1
1777485265.39359 | 27468 | -2.305447 | nan | nan | nan | nan | 1
1777485265.49569 | 27570 | -2.50339 | nan | nan | nan | nan | 1
1777485266.05754 | 28132 | -2.276125 | nan | nan | nan | nan | 1
1777485266.30204 | 28376 | -2.282701 | nan | nan | nan | nan | 1
1777485266.51301 | 28587 | -2.509012 | nan | nan | nan | nan | 1
1777485266.90451 | 28979 | -2.343288 | nan | nan | nan | nan | 1
1777485267.09178 | 29166 | -3.30075 | nan | nan | nan | nan | 1
1777485267.48303 | 29557 | 25.250154 | nan | nan | nan | nan | 0
1777485267.73414 | 29809 | -2.46727 | nan | nan | nan | nan | 1
1777485268.4834 | 30557 | 69.667221 | nan | nan | nan | nan | 0
1777485268.70077 | 30775 | -2.326362 | nan | nan | nan | nan | 1
1777485269.05831 | 31132 | -2.79076 | nan | nan | nan | nan | 1
1777485269.12565 | 31200 | -2.488589 | nan | nan | nan | nan | 1
1777485269.59213 | 31666 | -2.015041 | nan | nan | nan | nan | 1
1777485269.64931 | 31724 | -2.281186 | nan | nan | nan | nan | 1
1777485270.02455 | 32098 | -2.466673 | nan | nan | nan | nan | 1
1777485270.43264 | 32507 | -4.543856 | nan | nan | nan | nan | 1
1777485271.70488 | 33779 | -37.666626 | nan | nan | nan | nan | 1
1777485272.0241 | 34098 | -2.463311 | nan | nan | nan | nan | 1
1777485272.3645 | 34439 | -2.460679 | nan | nan | nan | nan | 1
1777485272.5346 | 34609 | -2.519651 | nan | nan | nan | nan | 1
1777485272.56839 | 34643 | -3.380163 | nan | nan | nan | nan | 1
1777485272.77945 | 34854 | -1.927539 | nan | nan | nan | nan | 1
1777485272.97307 | 35047 | -2.989615 | nan | nan | nan | nan | 1
1777485273.33107 | 35405 | -2.349902 | nan | nan | nan | nan | 1
1777485273.48345 | 35558 | -3.191502 | nan | nan | nan | nan | 1
1777485273.51746 | 35592 | -4.650019 | nan | nan | nan | nan | 1
1777485273.87526 | 35949 | -30.714109 | nan | nan | nan | nan | 1
1777485274.05817 | 36133 | -2.65451 | nan | nan | nan | nan | 1
1777485274.14322 | 36218 | -2.645638 | nan | nan | nan | nan | 1
1777485274.87607 | 36949 | 13.571452 | nan | nan | nan | nan | 0
1777485275.02602 | 37099 | -2.783924 | nan | nan | nan | nan | 1
1777485275.58624 | 37660 | -2.258335 | nan | nan | nan | nan | 1
1777485275.95025 | 38024 | -2.205995 | nan | nan | nan | nan | 1
1777485276.0587 | 38133 | -2.303035 | nan | nan | nan | nan | 1
1777485276.60351 | 38678 | -2.208892 | nan | nan | nan | nan | 1
1777485276.68834 | 38763 | -2.233768 | nan | nan | nan | nan | 1
1777485277.00808 | 39082 | -2.439467 | nan | nan | nan | nan | 1
1777485277.12706 | 39201 | -2.580194 | nan | nan | nan | nan | 1
1777485277.29766 | 39371 | -2.303283 | nan | nan | nan | nan | 1
1777485277.51859 | 39593 | -2.387501 | nan | nan | nan | nan | 1
1777485277.73987 | 39814 | -4.129406 | nan | nan | nan | nan | 1
1777485278.60389 | 40678 | -2.782024 | nan | nan | nan | nan | 1
1777485279.08432 | 41158 | -2.508937 | nan | nan | nan | nan | 1
1777485279.64587 | 41720 | -2.762721 | nan | nan | nan | nan | 1
1777485280.0174 | 42090 | -2.371435 | nan | nan | nan | nan | 1
1777485280.13878 | 42210 | -2.48559 | nan | nan | nan | nan | 1
1777485280.45893 | 42533 | -2.663467 | nan | nan | nan | nan | 1
1777485281.44196 | 43516 | -2.629632 | nan | nan | nan | nan | 1
1777485282.42138 | 44495 | -2.789731 | nan | nan | nan | nan | 1
1777485284.74533 | 46819 | -1.800002 | nan | nan | nan | nan | 1
1777485284.91533 | 46989 | -9.068959 | nan | nan | nan | nan | 1
1777485285.42201 | 47496 | -2.262715 | nan | nan | nan | nan | 1
1777485285.54095 | 47615 | -2.444697 | nan | nan | nan | nan | 1
1777485285.98358 | 48057 | -17.666582 | nan | nan | nan | nan | 1
1777485286.09198 | 48166 | -1.865772 | nan | nan | nan | nan | 1
1777485286.57549 | 48649 | -2.400003 | nan | nan | nan | nan | 1
1777485287.57538 | 49649 | -2.717704 | nan | nan | nan | nan | 1
1777485288.15393 | 50228 | -2.823542 | nan | nan | nan | nan | 1
1777485288.57547 | 50649 | -2.775062 | nan | nan | nan | nan | 1
1777485289.01794 | 51092 | -2.654683 | nan | nan | nan | nan | 1
1777485289.03481 | 51109 | -2.705165 | nan | nan | nan | nan | 1
1777485290.23942 | 52313 | -2.774192 | nan | nan | nan | nan | 1
1777485290.37596 | 52449 | -94.998489 | nan | nan | nan | nan | 1
1777485348.00447 | 110077 | 1.38816 | nan | nan | nan | nan | 0
1777485348.33454 | 110408 | 1.38836 | nan | nan | nan | nan | 0
1777485349.62109 | 111694 | 1.384067 | nan | nan | nan | nan | 0
1777485351.31863 | 113391 | 1.385821 | nan | nan | nan | nan | 0
1777485351.89722 | 113970 | 1.410458 | nan | nan | nan | nan | 0
1777485352.36811 | 114441 | 1.384109 | nan | nan | nan | nan | 0
1777485353.59194 | 115665 | 1.388161 | nan | nan | nan | nan | 0
1777485353.78109 | 115854 | 1.3927 | nan | nan | nan | nan | 0
1777485354.97642 | 117049 | 1.389686 | nan | nan | nan | nan | 0
1777485358.3604 | 120433 | 1.539071 | nan | nan | nan | nan | 0
1777485358.6784 | 120751 | 1.55294 | nan | nan | nan | nan | 0
1777485359.18935 | 121262 | 1.552088 | nan | nan | nan | nan | 0
1777485360.43637 | 122509 | 1.560067 | nan | nan | nan | nan | 0
1777485361.48626 | 123559 | 1.55581 | nan | nan | nan | nan | 0
1777485363.7058 | 125777 | 1.2868 | nan | nan | nan | nan | 0
1777485365.58777 | 127661 | 1.239418 | nan | nan | nan | nan | 0
1777485366.08664 | 128159 | 1.229271 | nan | nan | nan | nan | 0
1777485366.42304 | 128496 | 1.216395 | nan | nan | nan | nan | 0
1777485369.18951 | 131262 | 1.219241 | nan | nan | nan | nan | 0
1777485370.43844 | 132511 | 1.214646 | nan | nan | nan | nan | 0
1777485372.473 | 134545 | 1.212475 | nan | nan | nan | nan | 0
1777485372.55793 | 134631 | 1.217566 | nan | nan | nan | nan | 0
1777485373.11253 | 135185 | 1.210465 | nan | nan | nan | nan | 0
1777485377.96069 | 140033 | 1.213015 | nan | nan | nan | nan | 0
1777485379.06058 | 141133 | 1.21486 | nan | nan | nan | nan | 0
1777485379.47242 | 141545 | 1.211171 | nan | nan | nan | nan | 0
1777485379.51298 | 141562 | 1.21104 | nan | nan | nan | nan | 0
1777485379.54467 | 141586 | 1.216572 | nan | nan | nan | nan | 0
1777485379.57558 | 141603 | 1.216061 | nan | nan | nan | nan | 0
1777485379.60735 | 141627 | 1.216596 | nan | nan | nan | nan | 0
1777485379.64785 | 141644 | 1.217357 | nan | nan | nan | nan | 0
1777485379.6767 | 141671 | 1.214313 | nan | nan | nan | nan | 0
1777485379.70541 | 141688 | 1.212987 | nan | nan | nan | nan | 0
1777485379.73609 | 141712 | 1.21494 | nan | nan | nan | nan | 0
1777485379.77007 | 141729 | 1.214585 | nan | nan | nan | nan | 0
1777485379.81262 | 141753 | 1.217254 | nan | nan | nan | nan | 0
1777485379.84121 | 141770 | 1.217357 | nan | nan | nan | nan | 0
1777485379.88295 | 141794 | 1.215589 | nan | nan | nan | nan | 0
1777485379.91324 | 141811 | 1.214807 | nan | nan | nan | nan | 0
1777485379.95628 | 141835 | 1.211338 | nan | nan | nan | nan | 0
1777485380.00337 | 141852 | 1.21355 | nan | nan | nan | nan | 0
1777485380.04775 | 141876 | 1.211371 | nan | nan | nan | nan | 0
1777485380.07728 | 141893 | 1.21158 | nan | nan | nan | nan | 0
1777485380.12359 | 141918 | 1.210499 | nan | nan | nan | nan | 0
1777485380.16363 | 141935 | 1.20956 | nan | nan | nan | nan | 0
1777485380.19288 | 141959 | 1.211774 | nan | nan | nan | nan | 0
1777485380.23365 | 141976 | 1.209719 | nan | nan | nan | nan | 0
1777485380.26297 | 142000 | 1.216592 | nan | nan | nan | nan | 0
1777485380.30326 | 142017 | 1.21588 | nan | nan | nan | nan | 0
1777485380.33072 | 142041 | 1.215816 | nan | nan | nan | nan | 0
1777485380.35764 | 142058 | 1.215682 | nan | nan | nan | nan | 0
1777485380.38469 | 142086 | 1.213428 | nan | nan | nan | nan | 0
1777485380.41171 | 142103 | 1.213536 | nan | nan | nan | nan | 0
1777485380.43826 | 142127 | 1.213014 | nan | nan | nan | nan | 0
1777485380.46498 | 142144 | 1.212281 | nan | nan | nan | nan | 0
1777485380.49136 | 142168 | 1.218762 | nan | nan | nan | nan | 0
1777485380.51704 | 142185 | 1.218598 | nan | nan | nan | nan | 0
1777485380.5425 | 142210 | 1.218754 | nan | nan | nan | nan | 0
1777485380.56811 | 142227 | 1.218804 | nan | nan | nan | nan | 0
1777485380.59378 | 142254 | 1.213188 | nan | nan | nan | nan | 0
1777485380.61914 | 142271 | 1.211089 | nan | nan | nan | nan | 0
1777485380.64472 | 142295 | 1.207746 | nan | nan | nan | nan | 0
1777485380.67005 | 142312 | 1.208095 | nan | nan | nan | nan | 0
1777485380.6959 | 142336 | 1.211752 | nan | nan | nan | nan | 0
1777485380.72184 | 142353 | 1.211548 | nan | nan | nan | nan | 0
1777485380.74746 | 142378 | 1.212077 | nan | nan | nan | nan | 0
1777485380.77345 | 142396 | 1.211972 | nan | nan | nan | nan | 0
1777485380.79974 | 142421 | 1.210678 | nan | nan | nan | nan | 0
1777485380.82501 | 142438 | 1.208922 | nan | nan | nan | nan | 0
1777485380.85118 | 142462 | 1.209924 | nan | nan | nan | nan | 0
1777485380.87647 | 142479 | 1.209637 | nan | nan | nan | nan | 0
1777485380.90235 | 142503 | 1.213018 | nan | nan | nan | nan | 0
1777485380.92781 | 142520 | 1.212166 | nan | nan | nan | nan | 0
1777485380.95338 | 142544 | 1.21207 | nan | nan | nan | nan | 0
1777485380.97883 | 142561 | 1.21244 | nan | nan | nan | nan | 0
1777485381.00474 | 142586 | 1.2122 | nan | nan | nan | nan | 0
1777485381.03058 | 142603 | 1.212595 | nan | nan | nan | nan | 0
1777485381.05608 | 142627 | 1.211752 | nan | nan | nan | nan | 0
1777485381.08154 | 142644 | 1.211014 | nan | nan | nan | nan | 0
1777485381.10712 | 142668 | 1.214897 | nan | nan | nan | nan | 0
1777485381.13255 | 142685 | 1.214197 | nan | nan | nan | nan | 0
1777485381.15818 | 142709 | 1.214674 | nan | nan | nan | nan | 0
1777485381.18338 | 142726 | 1.21471 | nan | nan | nan | nan | 0
1777485381.20915 | 142752 | 1.213819 | nan | nan | nan | nan | 0
1777485381.23497 | 142769 | 1.213652 | nan | nan | nan | nan | 0
1777485381.2606 | 142793 | 1.213158 | nan | nan | nan | nan | 0
1777485381.2859 | 142810 | 1.21432 | nan | nan | nan | nan | 0
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

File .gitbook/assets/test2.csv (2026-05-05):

host_time_s | device_millis | vswr | forward_v | reverse_v | motor1_pos_rad | motor2_pos_rad | at_match
1777487564.78512 | 10230 | -2.407412 | nan | nan | 1.226187 | 1.57571 | 1
1777487565.00624 | 10451 | -2.553628 | nan | nan | 1.226187 | 1.57571 | 1
1777487565.31243 | 10757 | -8.304333 | nan | nan | 1.226187 | 1.57571 | 1
1777487565.92295 | 11366 | -2.469487 | nan | nan | 1.138806 | 1.488329 | 1
1777487566.51745 | 11961 | -3.829265 | nan | nan | 1.138806 | 1.488329 | 1
1777487566.83655 | 12281 | -2.401398 | nan | nan | 1.051425 | 1.57571 | 1
1777487566.97256 | 12417 | -2.400482 | nan | nan | 1.051425 | 1.57571 | 1
1777487568.77321 | 14217 | -12.272709 | nan | nan | 0.964049 | 1.488329 | 1
1777487569.00446 | 14449 | -2.000003 | nan | nan | 0.876678 | 1.569819 | 1
1777487569.05548 | 14500 | -2.166669 | nan | nan | 0.876678 | 1.569819 | 1
1777487569.07244 | 14517 | -2.160442 | nan | nan | 0.876678 | 1.569819 | 1
1777487569.46456 | 14909 | -2.055324 | nan | nan | 0.876678 | 1.569819 | 1
1777487569.56604 | 15011 | -2.006497 | nan | nan | 0.876678 | 1.569819 | 1
1777487570.00452 | 15449 | -2.24893 | nan | nan | 0.789308 | 1.482439 | 1
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

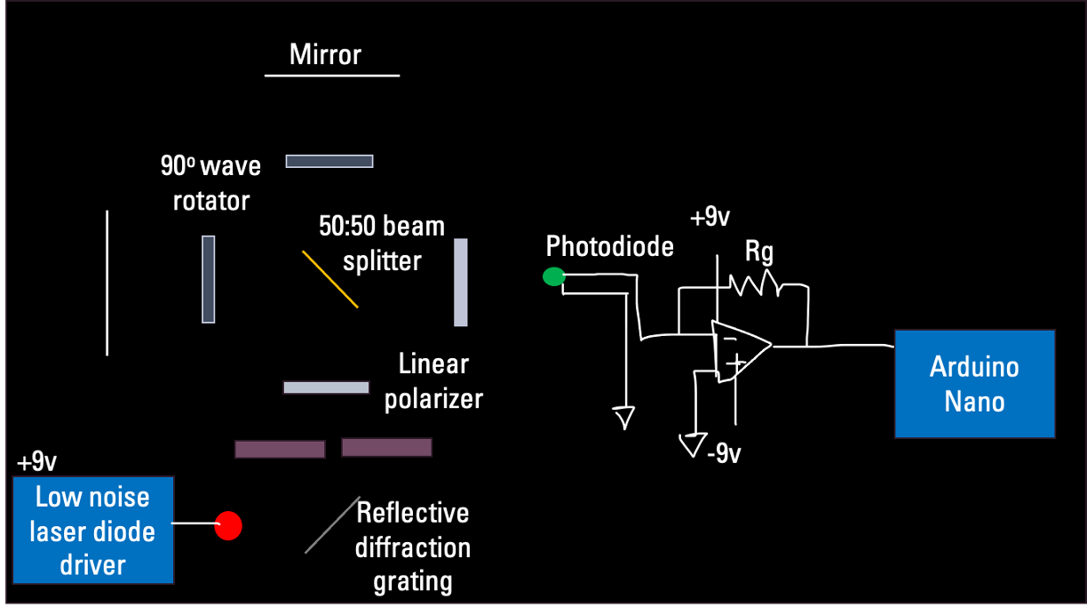
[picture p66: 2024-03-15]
fab-toolkit/metrology-characterization/interf_diagram_0.png

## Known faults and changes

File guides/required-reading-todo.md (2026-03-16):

# Contribution Guidlines

The goal function of the Hacker Fab is to never debug the same thing twice.

We operate under different constraints from the semiconductor fab industry. This allows us to curb a lot of complexity.

### Goals:

1. Low cost
2. Create the simplest designs possible
   1. Increase reliability
   2. Reduce manufacturing complexity
3. Minimal danger
4. Small size
5. Minimize required infrastructure
6. No cleanroom needed
7. Highly sourcable materials

### Things to include in documentation:

* BOM
* Build instructions
* Required tooling for build
* Required infrastructure
* Pics/diagrams
* CAD
* Testing/Verification
* SOP(s)
* Contact(s) (discord username, email, linkedin, etc.)

### On Improvement

Central to the Hacker Fab is fast turnaround hardware development - it’s in the name. This means extremely fast hardware prototyping, and with that comes the need for iteration. The careful design constraints placed on all projects and focus on documentation enables someone else to iterate on anything developed in the Hacker Fab. Improvement to a V1, V2, Vn of a design means

1. Directly improving upon a tool’s functionality&#x20;
   1. Precision&#x20;
   2. Reliability&#x20;
   3. Throughput&#x20;
   4. New features
   5. Safety

But there are other equally important ways to improve a design. Every tool version should try to be:

2. Easier to manufacture than the last
   1. Reduce number of tools required to manufacture
   2. Reduce # of vendors, lead time, BOM length
3. Better documented than the last
   1. Tool specs as close to first principles as possible
   2. Every tool spec should have a standardized test for others to verify performance
   3. Explain working principles to the detail of variables we can control (no more, no less). Referenced sources.
4. More “closed-loop” than the last
   1. In-situ sensors
   2. Calibration software should be more generalizable (“now you can use any camera…any piezo with draw distance in range X to Y…”)

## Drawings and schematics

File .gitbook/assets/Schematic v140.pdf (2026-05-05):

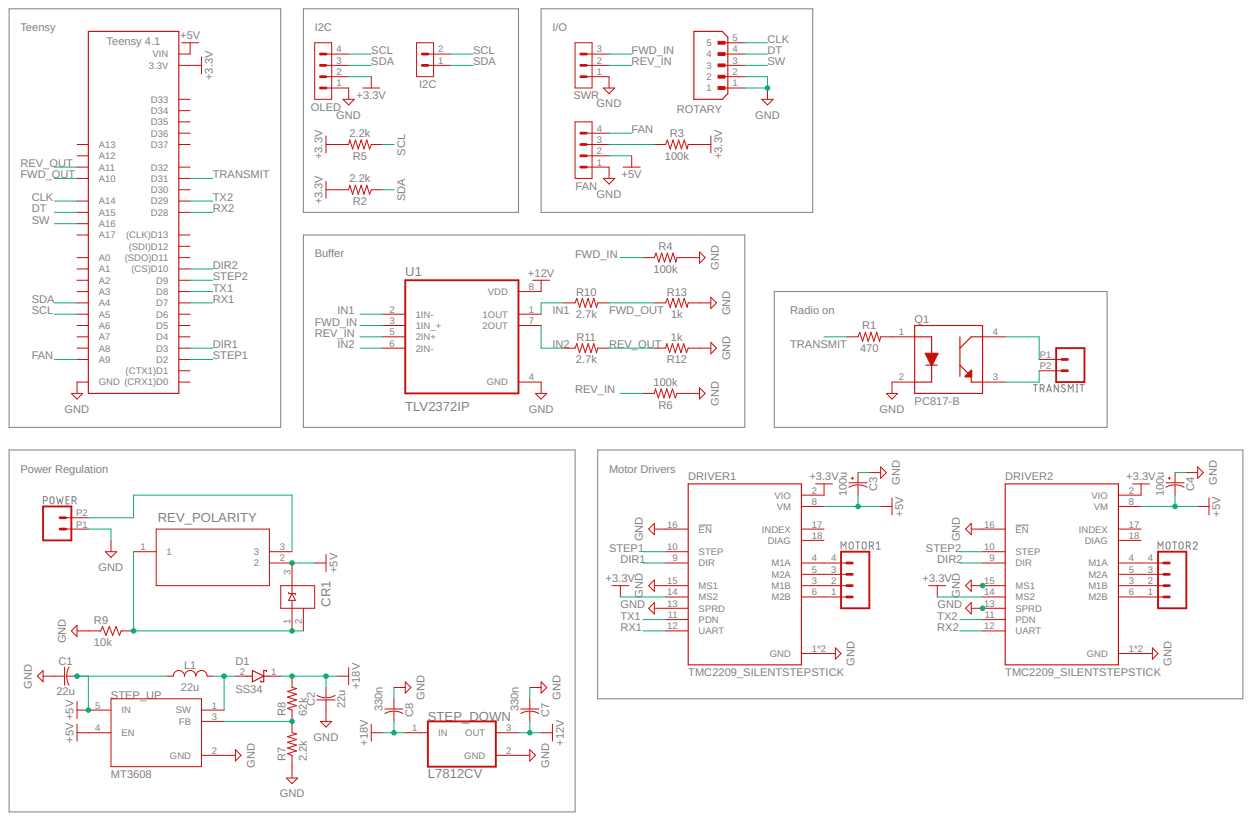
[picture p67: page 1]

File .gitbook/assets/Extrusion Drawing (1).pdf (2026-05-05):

2

1

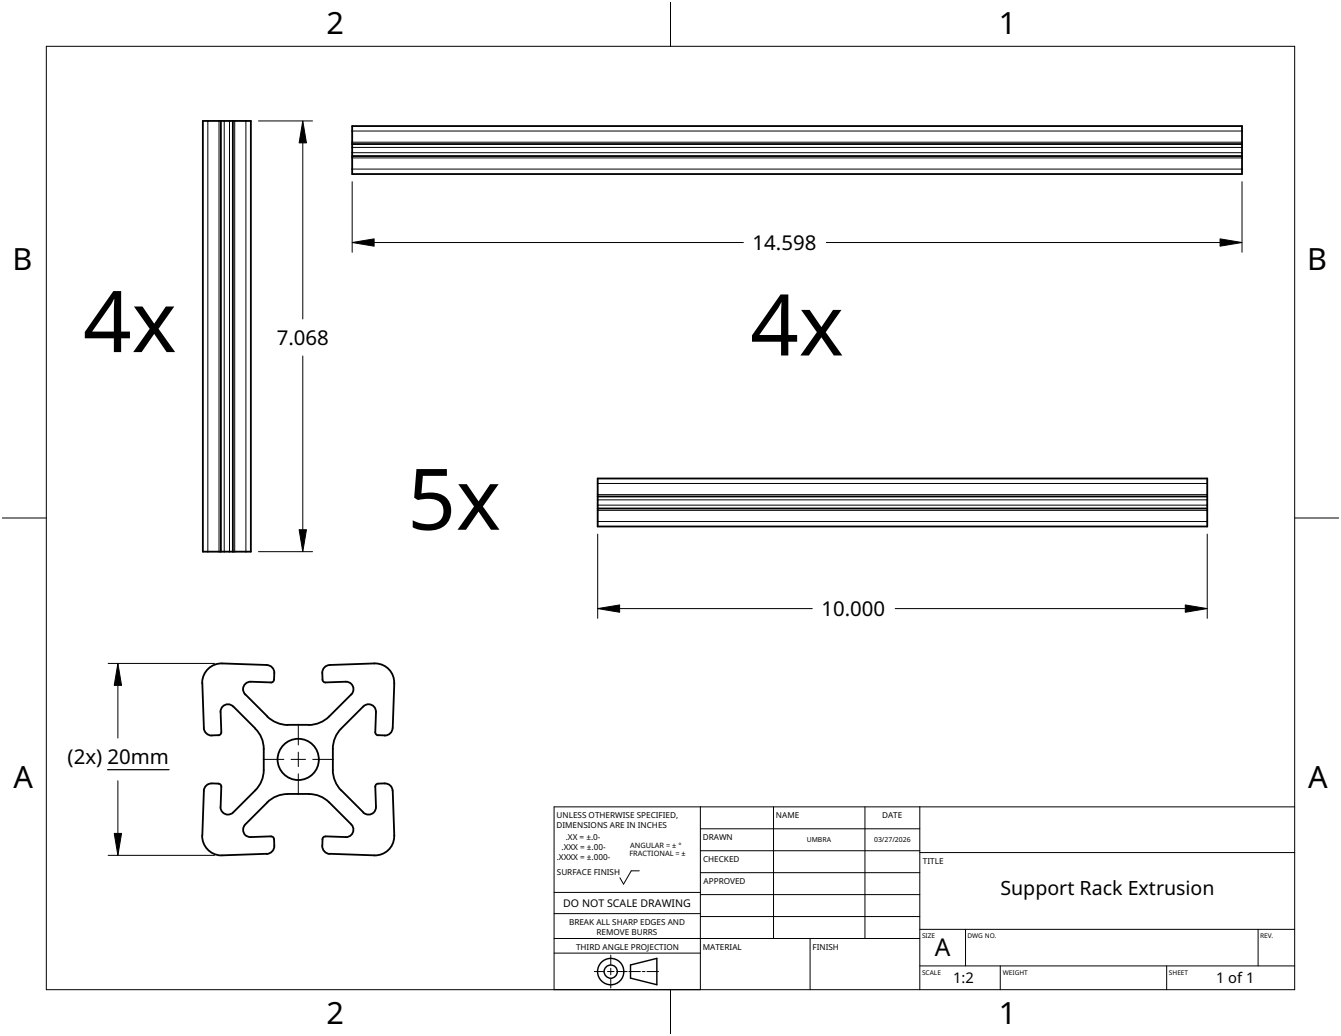
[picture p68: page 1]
MATERIAL; FINISH

UNLESS OTHERWISE SPECIFIED, DIMENSIONS ARE IN INCHES .XX = ±.0-ANGULAR = ± ° .XXX = ±.00-FRACTIONAL = ± .XXXX = ±.000-SURFACE FINISH | | NAME | DATE

DRAWN | UMBRA | 03/27/2026

CHECKED | | | TITLE Support Rack Extrusion

APPROVED

DO NOT SCALE DRAWING
BREAK ALL SHARP EDGES AND
REMOVE BURRS
THIRD ANGLE PROJECTION

SIZE A | DWG NO. | REV.

SCALE 1:2 | WEIGHT | SHEET 1 of 1

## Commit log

2023-10-31 GITBOOK-27: changed name of patterning SOP to include stepper V1
2023-11-06 GITBOOK-30: Evaporator Assembly Documentation
2023-11-25 GITBOOK-37: Attach Pump
2023-12-17 GITBOOK-53: Added wafer cleaning, hotplate, and pipette images
2024-01-16 GITBOOK-48: stepper v2 hardware desc and updating build manual template
2024-01-17 GITBOOK-55: Updated patterning manual for stepper V2.
2024-01-19 GITBOOK-60: don't suck too much liquid in pipette
2024-01-25 GITBOOK-64: update SOG SOP temperature profile
2024-01-31 GITBOOK-66: Stepper V2 build and template
    [StepperV2_Thorlabs_BOM.csv]
2024-01-31 GITBOOK-67: small cleanup stepper v2 build
2024-02-23 GITBOOK-78: stepper v2 build
2024-02-27 GITBOOK-80: completed optics assembly
2024-02-27 GITBOOK-81: stage 3d print and assemble
2024-03-15 Sketched diagram for stepper v3 interferometer
2024-03-15 Create interferometer.md
    Start documentation for stepper v3 parts
2024-03-15 GITBOOK-82: Finished 3d print assemble and mechanical integration
2024-03-27 Update probe-station-sop.md with more detailed setup and cleanup, as well as information about specific experiments (IV curves for transistors and resistors) and pictures
2024-04-07 GITBOOK-89: removed WIP from stepper V2
2024-04-10 GITBOOK-96: updated build-a-fab, home page, current fab capabilities 4/10
2024-05-01 Create DIY Tube Furnace Directory
2024-07-02 GITBOOK-112: Stepper V2 software installation updates
2024-07-11 GITBOOK-115: Added UV info to Safety and moved section; added "Troubleshooting" with camera bands removal steps
2024-08-06 GITBOOK-118: update stepper V2 BOM - optics cost
2024-09-03 GITBOOK-121: Updated BOM cost and UV LED link
2024-09-03 GITBOOK-120: Revise Stepper SOP for updated GUI software
2024-12-16 Update database-sop.md
    (User Flow, Challenges/Problems, Planned Improvements & Final Comment)
2025-01-20 GITBOOK-175: Jay's Jan 20 changes - tube furnace sop revisions
2025-02-27 GITBOOK-436: Add note about missing heatsink file in PCB ordering instructions
2025-03-10 GITBOOK-460: Sky: Mid-semester docs
    [v2.1-thorlabs.csv]
2025-03-16 GITBOOK-470: Updates to BOM, Basler camera, software setup
2025-03-20 GITBOOK-501: zero.offbyfour's Mar 20 changes
    [ECP5UMcsfBGA285Migration.csv]
2025-10-21 GITBOOK-707: Joel's Oct 9 changes - alternative stepper projector
2026-04-06 GITBOOK-765: No subject
    [Sputtered_Gate_NMOS_S26.xlsx]
2026-04-07 GITBOOK-758: Andrew Csanady's Changes to Case Western's site
2026-04-10 GITBOOK-771: No subject
    [4 point probe data 150nm thick Al.csv]
2026-04-22 GITBOOK-778: Updated current capabilities and ongoing projects section
2026-05-05 GITBOOK-794: Polysilicon Resistor Sub Page
2026-05-05 GITBOOK-799: Automated Sputtering Impedance Matching
    [test1.csv, test2.csv]
2026-05-05 GITBOOK-817: Micromanipulator assembly
2026-05-05 GITBOOK-814: Heating System for 2D Crystal Stacking and Nanopositioner Created
2026-05-05 GITBOOK-821: init for 2d stacking bot doc
    [Mounts - Microscope Ext. Bracket.stl, Mounts - Slide Mount.stl, Nanopositioner Mount - MotorMount_KM.stl, Nanopositioner Mount - MotorMount_KM_1.stl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]
2026-05-05 GITBOOK-812: Stepper v2.1 updates
2026-05-16 GITBOOK-830: Stepper Manual and other small fixes
2026-05-30 GITBOOK-834: Litho current limit fix
2026-06-05 GITBOOK-838: New onshape document for Motion Stage 3D Printed Parts
2026-06-09 GITBOOK-842: litho pcb assembly notes
2026-06-17 GITBOOK-843: update proximity switch circuit docs
